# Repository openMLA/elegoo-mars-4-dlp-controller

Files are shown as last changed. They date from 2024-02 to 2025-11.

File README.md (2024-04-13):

# Raspberry Pi hat for Elegoo Mars 4 DLP board 

A hat for the raspberry pi that allows a resin 3D printer's **UV light** projector to be controlled. Note that this is (in direct form) only suitable for the projector in the Mars 4 DLP. If you have other boards check out the repository for the [Anycubic Photon Ultra](https://github.com/openMLA/photon-ultra-controller), or get in touch for modifications needed. 

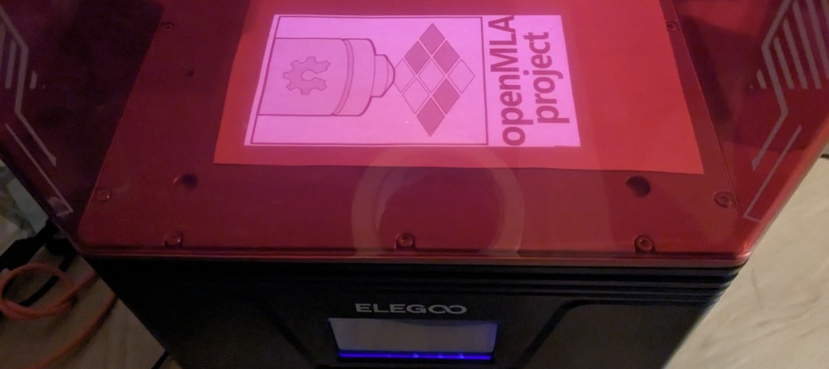
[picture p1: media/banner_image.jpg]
banner image showing custom image being displayed on the UV projector


The designs in this repository then allow you to project arbitrary **2560x1440** images with UV light on a surface. The native projected pixel size is **50μm**, making PCB fabrication an interesting application. All you would need is a bit of glue code to convert the Gerber files to a rasterised image and then you could easily use the existing 3D printer frame to expose PCB boards. Since you have all the files and access to the code, you can easily tune it to whatever production needs you have.

The UV projector of the Elegoo Mars 4 DLP is [developed and produced by Anhua (D63ZS50B)](https://www.anhuaoe.com/en/industriause/info.aspx?itemid=2694), and seems to be this variety. Under the hood it uses the Texas Instruments DLP300s or DLP301s digital micromirror array.

> [!NOTE]  
> While PCB fabrication is the most straightforward application for this board, this is actually developed as part of an effort towards an open hardware photolithography system. Check out the [openMLA organisation](https://github.com/openMLA/) for more info.

> If you have a projector using the DLPC1438 that uses the parallel video interface (rather than SPI) then you can check out the [PCB design and implementation for the Anycubic Photon Ultra](https://github.com/openMLA/photon-ultra-controller) projector.

### 🚀 At a glance

Running an SPI clock of ~125MHz it takes:

* ~0.75s to send a full 1440p image to the projector
* ~0.18s to send a 720p image to projector

Arbitrary sections of the display can be updated for even shorter transfer times. Note the maximum framerate (below) and that due to technical reasons the smallest image block that can be sent (in terms of transfer size) is 128x2 pixels. 

The image is stored in a buffer in the FPGA, so you can incrementally build or update an image, if that saves you time or makes your life easier.

The max achievable framerate seems to be about 10Hz (as there are some artefacts if you update faster). This is not a hard limit I suspect, and it may be possible to get closer to the display signal framerate of 60Hz.

### 💡 Sourcing the Projector

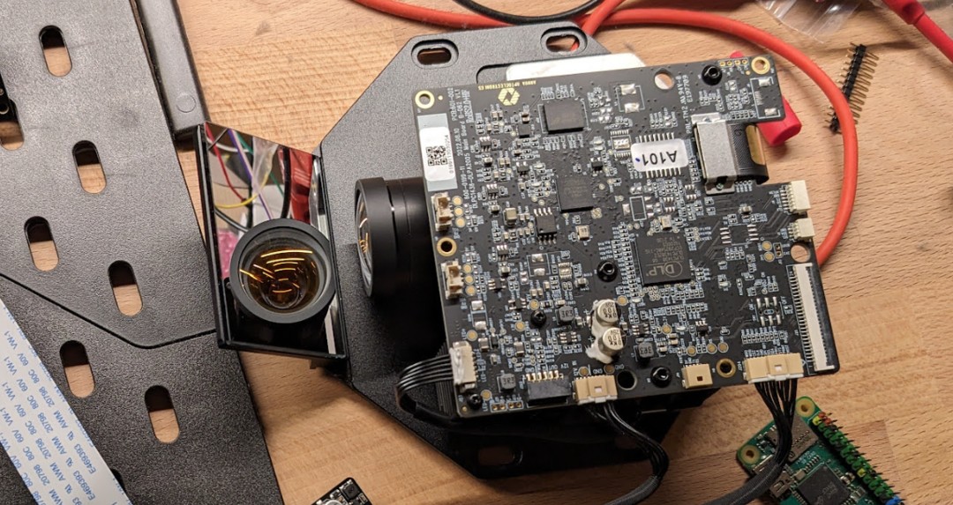
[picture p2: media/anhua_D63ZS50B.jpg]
the anhua projector taken from the Elegoo Mars 4 DLP


The easiest and cheapest way to source the projector is to buy a Elegoo Mars 4 DLP. At the time of writing (2024-02-02) the resin printer can be purchased in the EU for 275 euro (discounted).

Alternatively, the projector can be purchased directly from Anhua; but there may be small differences in the heatsink, LED source and other items. Also expect to pay a premium due to shipping, broker cost etc.

### 📃 Project BOM

The total costs for the project consists of 3 parts:

| Expense Description        | Cost  |
| -------------------------- | ----- |
| Elegoo Mars 4 DLP          | 274   |
| Electronics/PCB            | 52.38 |
| Enclosure/3D printed parts | -     |

_The PCB costs are further broken down [in the BOM in the PCB directory](./PCB/README.md)_

### 🎁 3D printable enclosure

A basic 3D printable enclosure is available in the enclosure directory. 

### 🛠 Disassembly 

Disassembly of the printer is not difficult, but I suggest you take a look at the points below before starting.

1. Make sure the projector is working properly by running the display test functions on the original elegoo board.
2. Raise the Z axis all the way to the top. It will only get in the way otherwise. You can also completely remove it later.
3. Remove the front panel. You will need allen keys and philips head screwdrivers. Carefully disconnect the display ribbon cable. Now you should be able to reach the connectors on the mainboard.
4. Disconnect all the connectors on the elegoo mainboard (the one not on top of the projector unit).
5. Undo the screws holding the bottom section of the printer enclosure in place. Now you carefully try to slide it forward and out of the way of the projector. This can be a bit tricky.
6. [optional] If don't want to use the projector in the original elegoo enclosure, you can remove it from the case with the 4 philips head screws holding it in place.

### 🛠 Assembly 

Assembly of the board is pretty straightforward. For completeness, here are the steps you will need to take.

1. Solder headers onto raspberry pi zero.
2. Assembly the custom PCB
3. Flash Raspberry Pi OS Lite onto an micro SD card. You can use [the raspberry pi imager](https://www.raspberrypi.com/software/) for this. Make sure to configure the wireless connection and ssh access in this step.
4. Attach the custom PCB to the raspberry pi zero header.
5. Plug in the 2 pico-claps connectors that were connected to the original elegoo mainboard
6. Plug in the original elegoo power supply to the barrel jack on the custom PCB.
7. Follow the more detailed [software setup](software-setup.md) to get the Pi up and running. 
8. [optional] if you want to use the projector inside the original enclosure, you can check out the instructions in [the enclosure directory](./enclosure/README.md)

### ✅ Future plans

2. Polish package with proper debug level logging and maybe proper formatted python documentation.
3. Add CRC16 checks. (low priority)

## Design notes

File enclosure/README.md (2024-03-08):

# Simple PCB Enclosure

To protect the raspberry pi zero and the PCB from damage and shorts you can 3D print the enclosure files in this directory.

Designed in FreeCAD. PCB was imported into FreeCAD with the [KiCAD StepUp plugin](https://www.kicad.org/external-tools/stepup/).

Step files can be sliced in e.g. PrusaSlicer.

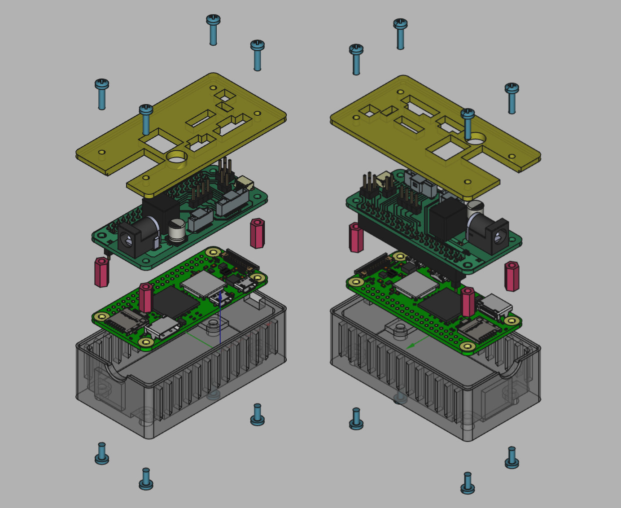
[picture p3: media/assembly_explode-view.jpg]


### Fasteners

In order to put this together you will also need:

* 4X M2.5 6mm screw
* 4X M2.5 10mm screw
* 4X DIN 6334 M2.5 10mm coupling nuts

### Using the enclosure inside the original Elegoo 3D printer

An alternative `.step` exists that has some extra mounting points that can mount onto the mounting points of the Projector.  That one is recommended if you want to keep using the 3D printer as a base for your project. You can of course also just print the normal case file and glue/tape it in place somewhere inside the case.

Some tips for assembling:

1. Tape the stepper, endswitch and USB power cables somewhere off to the side. Otherwise they may end up blocking the light from the projector.
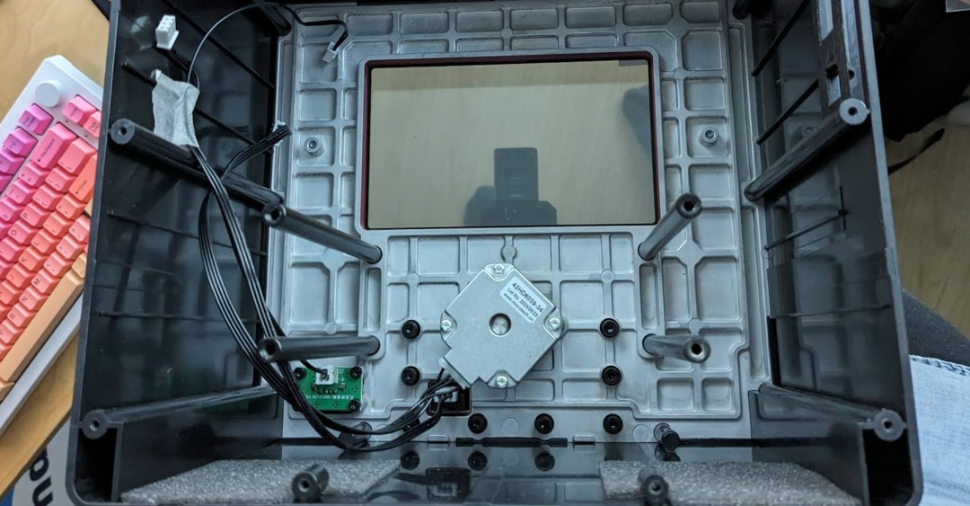
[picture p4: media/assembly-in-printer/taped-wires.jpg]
   
2. Avoid straining the pico-clasp cables
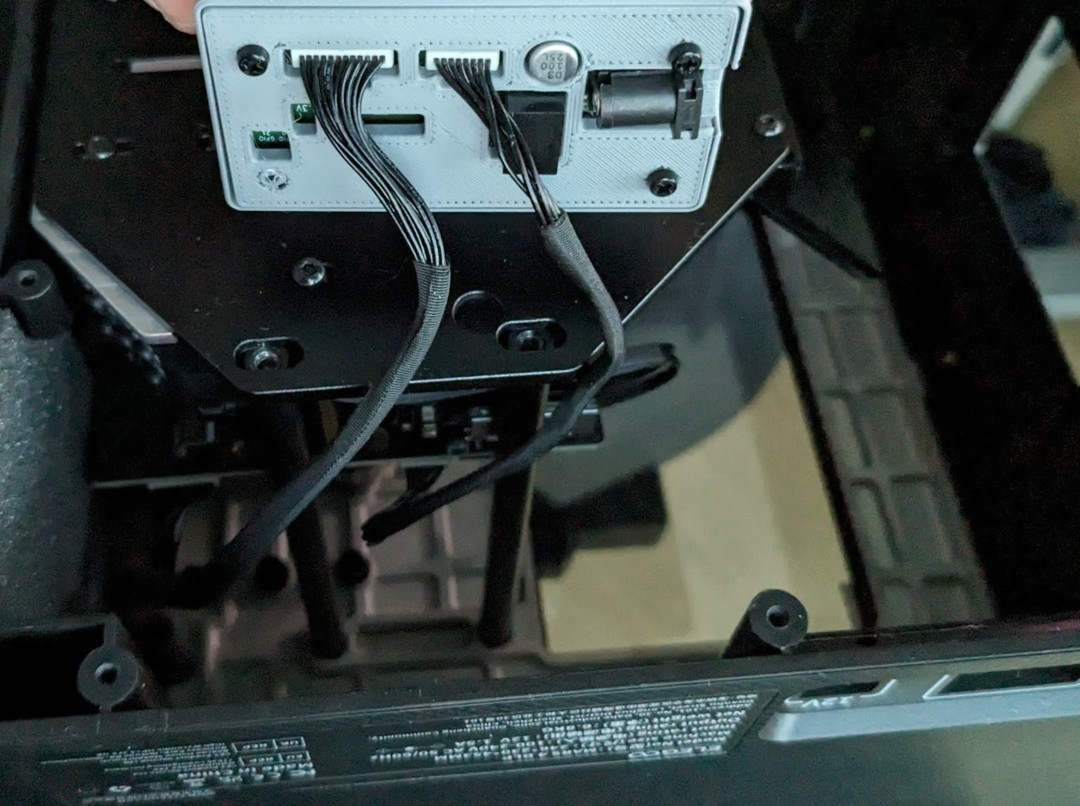
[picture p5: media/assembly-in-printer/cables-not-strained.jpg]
   
3. Route the original 12V power supply through one of the now open ports. It's not very elegant, so if you are interested you can modify the PCB or the case design to nicely route the power cable
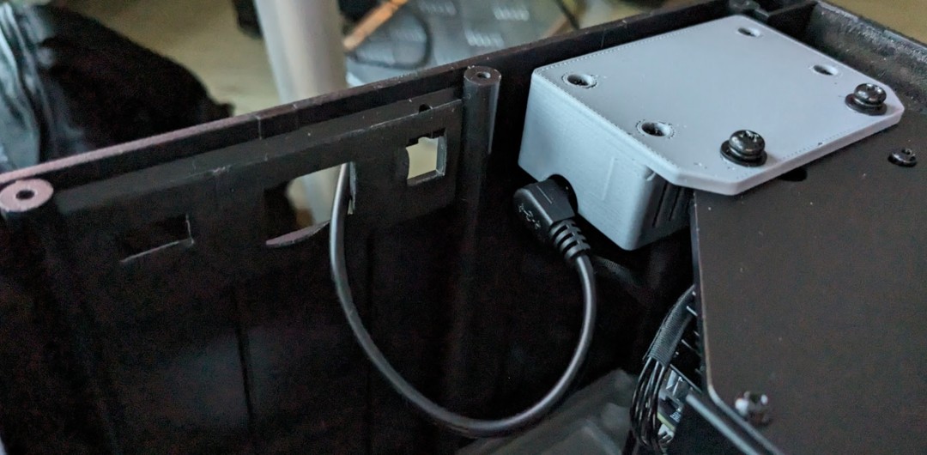
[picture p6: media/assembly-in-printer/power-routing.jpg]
   
4. Tape these open ports shut, to prevent leakage of UV light.
5. Keep the original touchscreen in place on the unit, as it will block the UV light. If you want to be extra secure, you can also apply some tape to the edges of the screen to really prevent UV leakage.

### External 3D models

The Model of the raspberry Pi zero 2 was downloaded from [the geekworm wiki](https://wiki.geekworm.com/Raspberry_Pi_Zero_2_W) on 28th of february 2023.

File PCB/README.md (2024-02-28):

# PCB design

To control the DMD with a raspberry pi, we need a very simple board that allows us to plug in the original Anhua board's connectors (Molex Pico-clasp). Check out [the schematic 🗺](elegoo-dlp-controller.pdf) for the quickest overview of all functionality.

To make our life a little easier, you can add an (optional) dc-dc converter that also converts the 12V to 5V and uses that to power the raspberry pi. This means you do not need to apply separate 5V power to the raspberry pi, and that the 12V needed for the Anhua board provided by the Elegoo Mars 4's power supply is enough to power everything.

Finally, the board breaks out some extra pins for adding your own extra custom bits. SPI and I2C connections, as well as some spare GPIO pins. This may be useful if you want to have exposure occur based on some sensor readout, or maybe tie UV exposure to a simple button for batch production where you don't want to send commands over SSH.

> [!IMPORTANT]  
> Not every connection has been verified to work. I suspect they are all fine since its not a very complex board or high frequency signals. At least the minimum set of pins required for data/exposure seem to work fine.

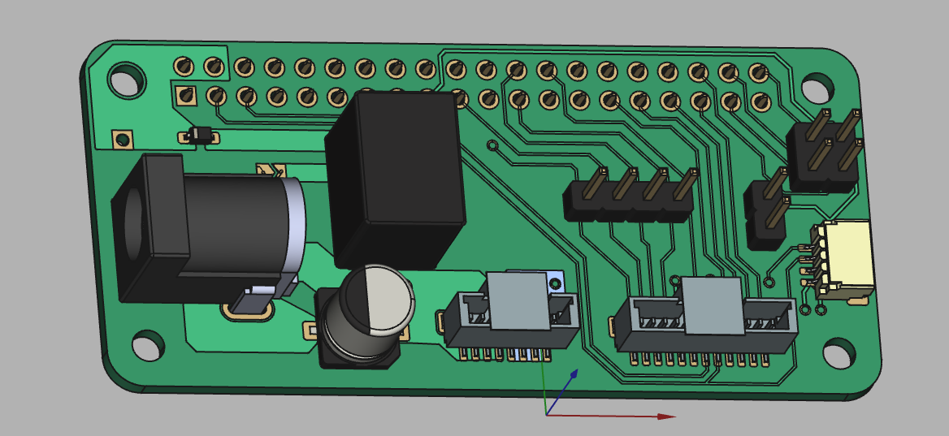
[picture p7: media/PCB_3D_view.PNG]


### Bill of materials

The costs below are indicative, as shipping cost and price changes may have occurred since writing this document. Check with KiCAD's schematic to see if it all up to date. All listed values are including taxes (21%).

| Description                | Supplier         | Supplier Part Number | Amount | Total Cost | Comment                                      |
| -------------------------- | ---------------- | -------------------- | ------ | ---------- | -------------------------------------------- |
| PCB manufacturing          | Aisler           |                      | 3      | 14         | MOC 3pcs                                     |
| Raspberry Pi Zero 2        | Mouser           | 358-SC0510           | 1      | 17         |                                              |
| Micro SD Card (32GB)       | Kiwi Electronics | TS32GUSDU1           | 1      | 10         | Whatever kind you want would work            |
| Raspberry pi header        | Kiwi Electronics | KW-2639              | 1      | 2          | or any basic, cheaper header                 |
| Raspberry pi header female | Kiwi Electronics | KW-1650              | 1      | 1.5        |                                              |
| JST SH 4-pin               | Mouser           | 474-PRT-14417        | 1      | 0.67       | Optional, allows i2c through  stemmaQT/QWIIC |
| Molex PicoClasp 12 pin     | Mouser           | 538-501331-1207      | 1      | 1.19       |                                              |
| Molex PicoClasp 8 pin      | Mouser           | 538-501331-0807      | 1      | 0.92       |                                              |
| Cui DC-DC converter        | Mouser           | 490-P78E05-1000      | 1      | 3.45       |                                              |
| Barreljack                 | Mouser           | 490-PJ-002B          | 1      | 0.79       |                                              |
| Schottky Diode             | Mouser           | 771-PMEG1020EJ-T/R   | 1      | 0.29       |                                              |
| 100uF capacitor            | Mouser           | 667-EEE-FN1E101UP    | 1      | 0.57       |                                              |
|                            |                  |                      |        |            |                                              |
| Total                      |                  |                      |        | 52.38      |                                              |

### Miscellaneous

* Board was designed in KiCAD 7.0
* I had the board fabricated at Aisler (Germany), at 14 euros (total) for 3 boards.

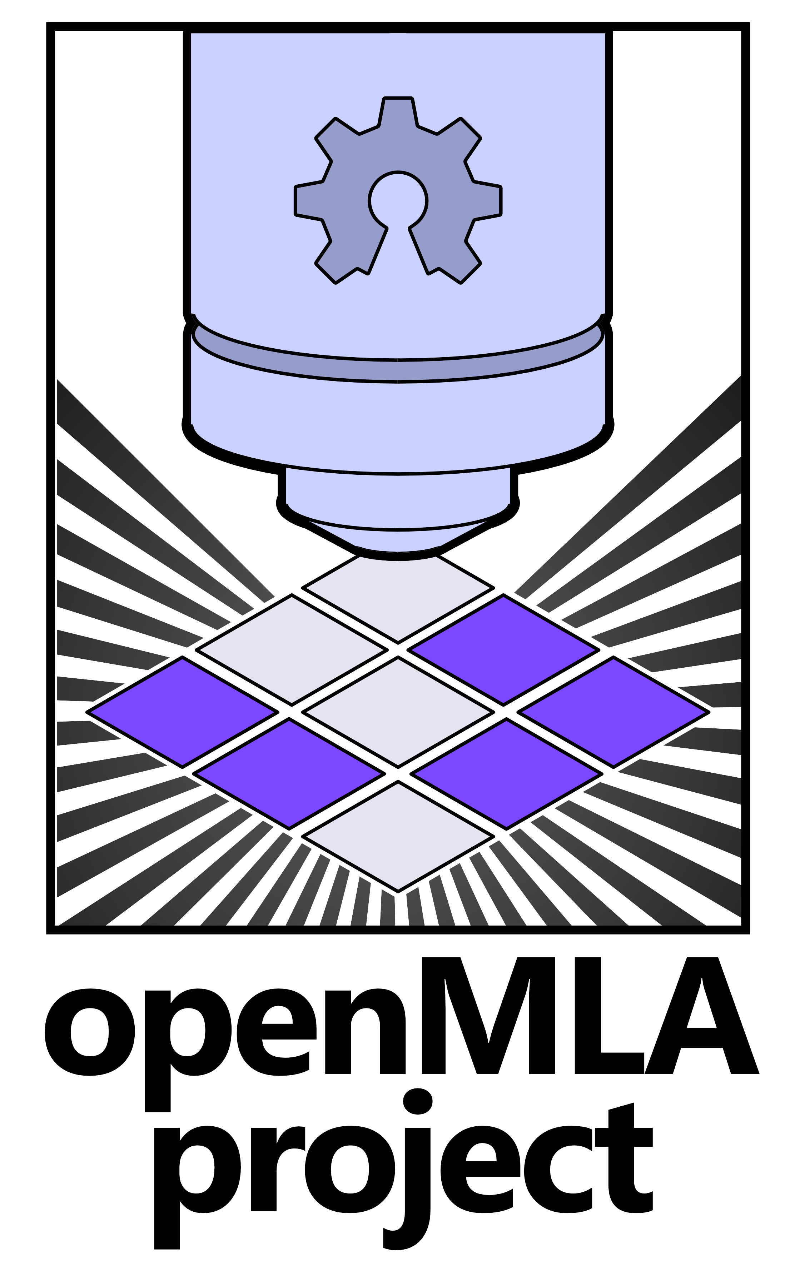
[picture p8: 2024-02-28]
PCB/board-assets/open-mla-tall - Copy.png

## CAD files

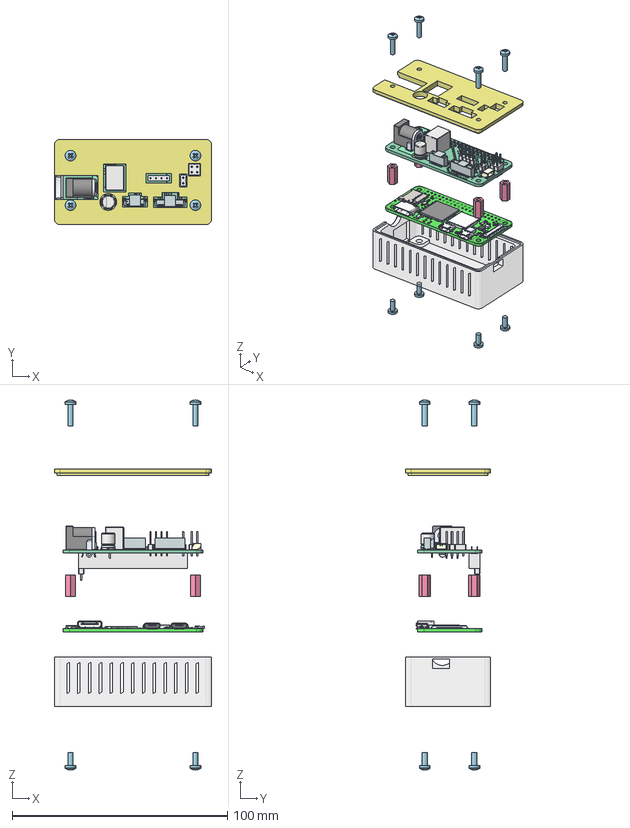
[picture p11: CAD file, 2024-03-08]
enclosure/dlp-controller-enclosure.FCStd
73.0 x 39.5 x 171.8 mm
enclosure-base
PCB, Raspberry Pi Zero 2 W
RP3A0-AU 2105 201221C, Raspberry Pi Zero 2 W
MicroUSB Port, Raspberry Pi Zero 2 W
MicroUSB Port, Raspberry Pi Zero 2 W001
MicroUSB Port, Raspberry Pi Zero 2 W002
MicroUSB Port, Raspberry Pi Zero 2 W003
MicroUSB Port, Raspberry Pi Zero 2 W004
MicroUSB Port, Raspberry Pi Zero 2 W005
MicroUSB Port, Raspberry Pi Zero 2 W006
SD Card Slot, Raspberry Pi Zero 2 W
SD Card Slot, Raspberry Pi Zero 2 W001
SD Card Slot, Raspberry Pi Zero 2 W002
SD Card Slot, Raspberry Pi Zero 2 W003
SD Card Slot, Raspberry Pi Zero 2 W004
SD Card Slot, Raspberry Pi Zero 2 W005
SD Card Slot, Raspberry Pi Zero 2 W006
SD Card Slot, Raspberry Pi Zero 2 W007
SD Card Slot, Raspberry Pi Zero 2 W008
SD Card Slot, Raspberry Pi Zero 2 W009
Wireless Module Cover, Raspberry Pi Zero 2 W
Crystal Resonator, Raspberry Pi Zero 2 W
LED, Raspberry Pi Zero 2 W
Diode, Schottky, Raspberry Pi Zero 2 W
54548-2271, 22 Pin FPC Connector, Raspberry Pi Zero 2 W
Mini HDMI Receptacle Port, Raspberry Pi Zero 2 W
PAM2306AYPKE, Switching Voltage Regulators Dual PWM Step-Down 40uA 1A 1.5MHz, Raspberry Pi Zero 2 W
RT9081A-1BGQZA, Fixed LDO Voltage Regulator, 0.8V-5.5Vin, 140mV drop, 1.25Vout, 0.5Aout, Raspberry Pi Zero 2 W_default
RT8088AWSC, IC Reg Buck Prog 3A Sync 15WLCSP, Raspberry Pi Zero 2 W_default
SMD Inductor, Configurable, Raspberry Pi Zero 2 W_L1
SMD Inductor, Configurable, Raspberry Pi Zero 2 W_L2
SMD Capacitor, Configurable, Raspberry Pi Zero 2 W_C1
SMD Capacitor, Configurable, Raspberry Pi Zero 2 W_C002
SMD Capacitor, Configurable, Raspberry Pi Zero 2 W_C003
MicroUSB Port, Raspberry Pi Zero 2 W008
MicroUSB Port, Raspberry Pi Zero 2 W009
MicroUSB Port, Raspberry Pi Zero 2 W010
MicroUSB Port, Raspberry Pi Zero 2 W011
MicroUSB Port, Raspberry Pi Zero 2 W012
MicroUSB Port, Raspberry Pi Zero 2 W013
MicroUSB Port, Raspberry Pi Zero 2 W014
SMD Capacitor, Configurable, Raspberry Pi Zero 2 W_C3
SMD Capacitor, Configurable, Raspberry Pi Zero 2 W_C005
SMD Capacitor, Configurable, Raspberry Pi Zero 2 W_C006
SMD Capacitor, Configurable, Raspberry Pi Zero 2 W_C008
SMD Capacitor, Configurable, Raspberry Pi Zero 2 W_C009
SMD Capacitor, Configurable, Raspberry Pi Zero 2 W_C010
SMD Capacitor, Configurable, Raspberry Pi Zero 2 W_C012
SMD Capacitor, Configurable, Raspberry Pi Zero 2 W_C013
SMD Capacitor, Configurable, Raspberry Pi Zero 2 W_C014
SMD Capacitor, Configurable, Raspberry Pi Zero 2 W_C016
SMD Capacitor, Configurable, Raspberry Pi Zero 2 W_C017
SMD Capacitor, Configurable, Raspberry Pi Zero 2 W_C018
SMD Capacitor, Configurable, Raspberry Pi Zero 2 W_C020
SMD Capacitor, Configurable, Raspberry Pi Zero 2 W_C021
SMD Capacitor, Configurable, Raspberry Pi Zero 2 W_C022
SMD Capacitor, Configurable, Raspberry Pi Zero 2 W_C024
SMD Capacitor, Configurable, Raspberry Pi Zero 2 W_C025
SMD Capacitor, Configurable, Raspberry Pi Zero 2 W_C026
SMD Capacitor, Configurable, Raspberry Pi Zero 2 W_C028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

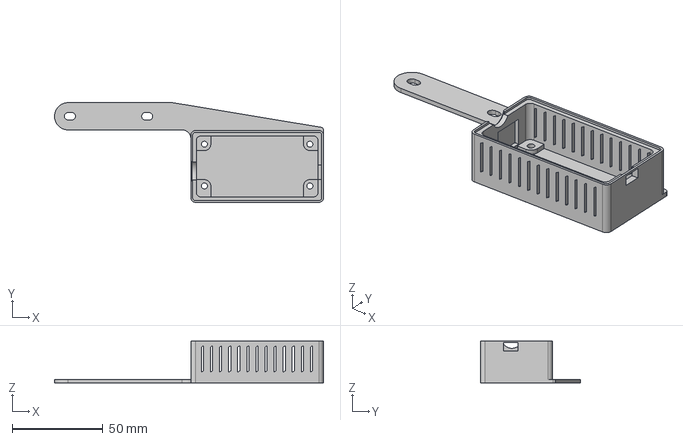
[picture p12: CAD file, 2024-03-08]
enclosure/step/enclosure-base-elegoo.step
148.0 x 54.9 x 23.0 mm

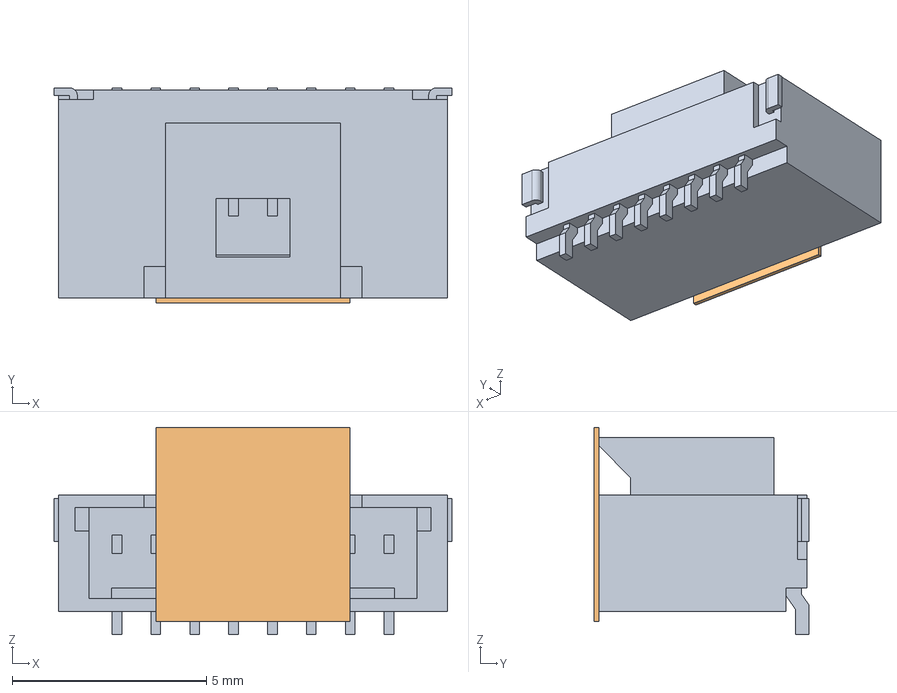
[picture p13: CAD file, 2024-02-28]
PCB/board-assets/molex_5013310807.stp
10.2 x 5.54 x 5.34 mm

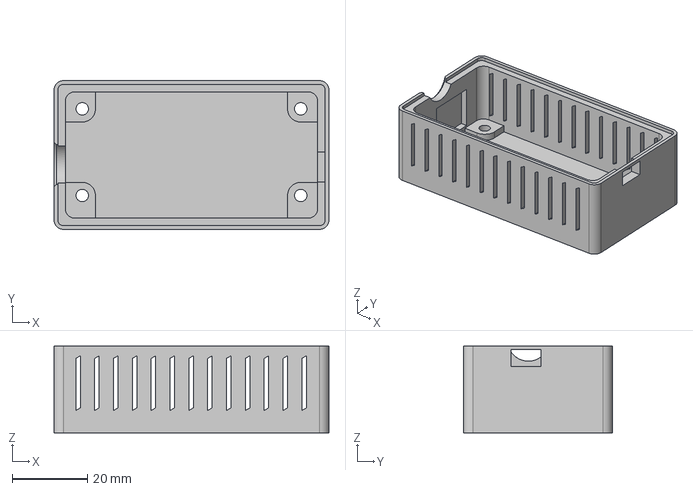
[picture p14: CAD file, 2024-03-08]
enclosure/step/enclosure-base.step
73.0 x 39.5 x 23.0 mm

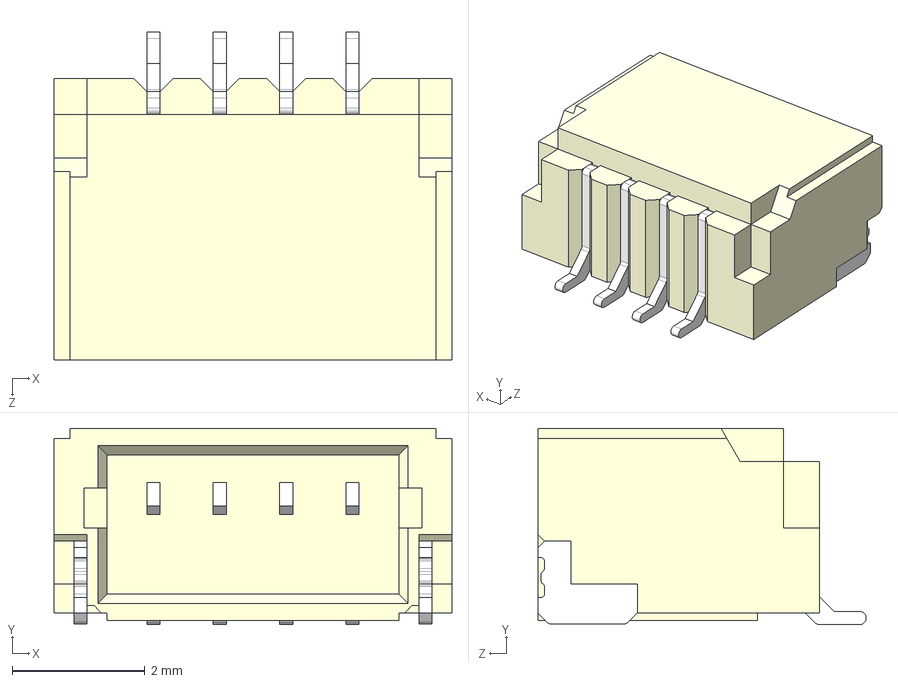
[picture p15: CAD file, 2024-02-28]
PCB/board-assets/PRT-14417--3DModel-STEP-SnapEDA.STEP
6.00 x 2.96 x 4.95 mm

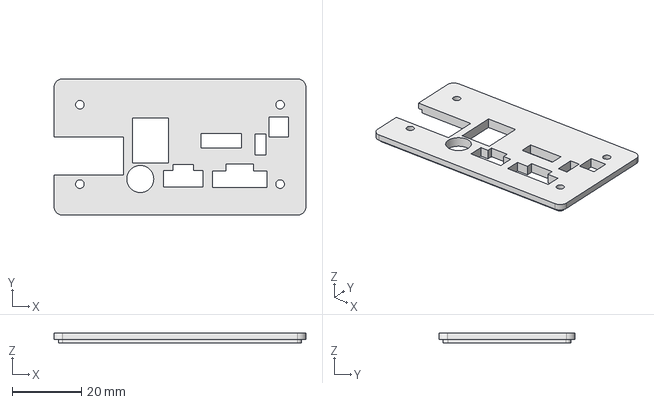
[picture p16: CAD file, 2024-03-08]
enclosure/step/enclosure-lid.step
73.0 x 39.5 x 3.00 mm

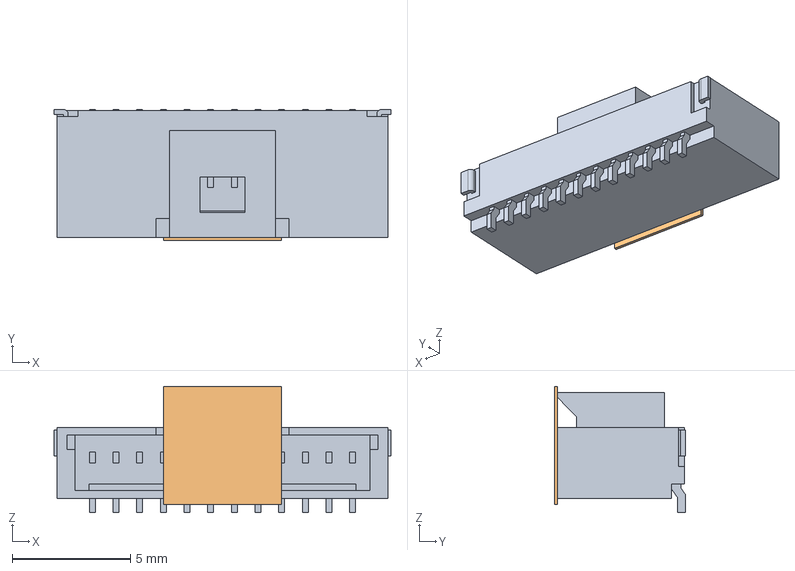
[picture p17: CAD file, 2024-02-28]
PCB/board-assets/molex_5013311207.stp
14.2 x 5.54 x 5.34 mm

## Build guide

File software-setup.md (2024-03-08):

## ⚙ configuring the Raspberry Pi for project

> [!NOTE]
>
> The following set of instructions assumes you are running Raspberry Pi OS Lite. 

We will need to get pip. Doesn't seem to get packaged by default.

```shell
sudo apt install python3-pip
```

and we need to enable I2C and SPI with the following commands

```shell
sudo raspi-config nonint do_i2c 0
```

```shell
sudo raspi-config nonint do_spi 0
```

We also need to increase the SPI buffer size, as the default is only 4096 bytes. To do so, we edit `cmdline.txt` by running

```shell
sudo nano /boot/cmdline.txt
```

and we add the following entry to increase the buffer size to 65536  bytes:

```
spidev.bufsiz=65536  
```

> [!IMPORTANT]
>
> Note that after setting these new values you will need to restart the raspberry pi for the changes to go into effect.

#### 🐍 Python packages

Finally, we will need to install some python packages:

```shell
sudo apt install python3-smbus
```

```shell
sudo apt install python3-spidev
```

```shell
sudo apt install python3-numpy
```

```shell
sudo apt install python3-pillow
```

> [!NOTE]
>
> For some reason Pi OS Lite doesn't love installing via pip, so the commands above are used. I am sure you could install it via pip with minimal effort.

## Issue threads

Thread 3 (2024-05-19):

### ISSUE TITLE
Using Rasbian Pi OS (64bit)

### ISSUE THREAD

**Issue by Hackerman2016** [openMLA/elegoo-mars-4-dlp-controller#3]
In the project, you have used the Rasbian Pi OS Lite. I was wondering if there is any specific reason for that. can I use the Rasbian Pi OS (64bit) instead, and would the same Python script work for that? Also, will the commands for installing Python libraries remain the same? Any help with this would be great. Thanks!

**Comment by NemoAndrea** [comment]
The normal raspberry Pi OS should work fine. It may be that the normal OS already has some of the dependencies installed (which isn't bad). I use the Lite version because I don't need a desktop environment anyway (just accessing the Pi over SSH), so then the Lite version will give better boot times and performance.

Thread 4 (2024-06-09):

openMLA/elegoo-mars-4-dlp-controller #4: Soldering 5V port on PCB

Hackerman2016, 2024-06-09:
So I have built the PCB according to the instructions, and I was wondering whether or not to solder the 5V port on the PCB, and after the PCB is complete, what is ideally the next step? I have to install the packages as specified on the pi and run the main.py, and it should work?

NemoAndrea, 2024-06-09:
The 5V pin on the PCB (assuming we are talking about the same pin), can be left out; it is just there in case you want to power something with the 5V from the pi/dcdc converter. 

If you are taking about the solder bridge: it should be soldered if you have a the  dc-dc converter (CUI P78E)  soldered in place; if you don't have the CUI, then it doesn't really matter if you close the solder bridge. 

> [!WARNING]
> Whatever you do, do not power the raspberry pi through USB and the CUI converter at the same time. It is **either** power through the USB connector of the pi (leave the 5V solder bridge empty, and leave out the CUI) **or** power through the 12V barrel jack with the CUI to provide the 5V power for the Pi.

If you have assembled the board and checked that the pi still works (I suggest you do this before connecting the projector). then you hook up the projector, follow the software packages instructions and then indeed try main.py.

If that all works you can start writing your own python code for your project  using the included code :)

Hackerman2016, 2024-06-10:
I have the dc-dc converter in place.
[image]
This is the 5V port I am talking about.

NemoAndrea, 2024-06-10:
Ah yes, that one you should bridge if you have the dc-dc converter installed. This connects the 12V to the input of the converter. 

To reiterate (to prevent damage), do not connect USB power to the pi if you also connect the 12V at the same time.

Hackerman2016, 2024-06-11:
Ah, okay. Great. Thanks a lot.

closed 2024-06-11 by Hackerman2016

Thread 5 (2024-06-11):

openMLA/elegoo-mars-4-dlp-controller #5: Regarding running the python code

Hackerman2016, 2024-06-11:
[image]

I have connected all the components and have managed to power on the printer after connecting the pcb and pi but as soon as I run the code I get this error. Any help with this will be appreciated. Also I have trouble in connecting the pi to the internet. Doing configuring the rasbian os 64 bit on the pi zero 2W I did the ssh settings but still somehow when I login on putty with the hostname I get an error saying hostname doesn't exist.

Hackerman2016, 2024-06-11:
Also when I am trying to increase the SPI buffer size I followed the steps mentioned in the document but I am unable to do it. I am getting this error.
[image]

NemoAndrea, 2024-06-25:
Hmm for the first point, could it be that you are running the python code on your local machine and not on the raspberry pi? If not then you need to install RPi.GPIO but I think that should definitely come with the default OS.

For the 2nd image, why is there `firmware` in the path?  It should just be `/boot/cmdline.txt`; that might fix it

Hackerman2016, 2024-06-26:
For the first point you were right I was trying to run it on local machine. Running it on Pi solved the issue and yeah about making changes in the /boot/cmdline.txt file, for me after running that command I get an error saying that the file has been shifted to /boot/firmware/cmdline.txt. That's why increasing the buffer size and stuff I have all done it in that file.

NemoAndrea, 2024-06-26:
Hmm, strange, I am not aware of this change. I guess there must be a file `cmdline.txt` somewhere on the system. Maybe you can post raspberry pi os version here, so that other people can figure out if they may be running a version with issues too.

Hackerman2016, 2024-06-27:
That is a difference I am not working with the OS lite and Pi Zero. I am working with the Raspberry Pi 3b+ and the standard Raspberry OS 64-bit.

NemoAndrea, 2024-08-06:
Okay, I will close this issue, as I think it would be better to make a more focussed new issue if you cannot figure it out. Nice to see you being able to get the project working (at least in parts!). 

If you run into issues where the documentation is wrong or even just unclear, let me know because that is super valuable for the project :)

closed 2024-08-06 by NemoAndrea

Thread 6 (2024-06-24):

openMLA/elegoo-mars-4-dlp-controller #6: Error while reading i2c port 1

Hackerman2016, 2024-06-24:
Hello,

I am trying to run the python script and I am getting an error where the i2c 1 port is undetectable.  I have tried adding these lines in the boot file 'dtparam=i2c_arm=on
dtparam=i2c1=on'   

Still I get the same error. Here is the error that I get:

  File "/home/pi/Desktop/UV_projector/controller.py", line 61, in __init__
    i2c_bus.read_byte(self.addr)  # check if i2c is already active. Then we are in [2]
    ^^^^^^^^^^^^^^^^^^^^^^^^^^^^
OSError: [Errno 5] Input/output error

During handling of the above exception, another exception occurred:

Traceback (most recent call last):
  File "/home/pi/Desktop/main.py", line 24, in <module>
    DMD = DLPC1438(i2c, spi)
          ^^^^^^^^^^^^^^^^^^
  File "/home/pi/Desktop/UV_projector/controller.py", line 85, in __init__
    while i2c_bus.read_byte(self.addr) == 0:  
          ^^^^^^^^^^^^^^^^^^^^^^^^^^^^
OSError: [Errno 5] Input/output error

NemoAndrea, 2024-06-25:
hmm, what does `i2cdetect -y 1` give?

Hackerman2016, 2024-06-26:
It gives a table where there are no addresses assigned. So it is just a table with dashes.

NemoAndrea, 2024-06-26:
Okay, so that means that the I2C hardware on the Pi is working.  I don't really know what is causing the issue; it certainly seems like the DLPC1438 is not starting properly. Do you see some LEDs lit up on the mainboard? Does it work if you run the code a few times (Sometimes it needs one run to get going; something not quite right about the power up cycle in the code)

Hackerman2016, 2024-06-28:
[image]

Do i need to solder these adapters too on the pcb or are they optional? What are their functions?

NemoAndrea, 2024-07-17:
> ![image0 (2)](https://private-user-images.githubusercontent.com/170014411/344107721-8f8bc00e-e9fa-4d8c-bf7a-1d914d15774f.jpeg?jwt=eyJhbGciOiJIUzI1NiIsInR5cCI6IkpXVCJ9.eyJpc3MiOiJnaXRodWIuY29tIiwiYXVkIjoicmF3LmdpdGh1YnVzZXJjb250ZW50LmNvbSIsImtleSI6ImtleTUiLCJleHAiOjE3MjEyMTc4NjcsIm5iZiI6MTcyMTIxNzU2NywicGF0aCI6Ii8xNzAwMTQ0MTEvMzQ0MTA3NzIxLThmOGJjMDBlLWU5ZmEtNGQ4Yy1iZjdhLTFkOTE0ZDE1Nzc0Zi5qcGVnP1gtQW16LUFsZ29yaXRobT1BV1M0LUhNQUMtU0hBMjU2JlgtQW16LUNyZWRlbnRpYWw9QUtJQVZDT0RZTFNBNTNQUUs0WkElMkYyMDI0MDcxNyUyRnVzLWVhc3QtMSUyRnMzJTJGYXdzNF9yZXF1ZXN0JlgtQW16LURhdGU9MjAyNDA3MTdUMTE1OTI3WiZYLUFtei1FeHBpcmVzPTMwMCZYLUFtei1TaWduYXR1cmU9ZDZkYTRiOWJhNDcyMjA0ODJmY2NmNzczMTM1OTYzNWYwOWJjNTlkZTQ0OTRiMTg1NDRlOGFiZGY4ZGU2NDRmOCZYLUFtei1TaWduZWRIZWFkZXJzPWhvc3QmYWN0b3JfaWQ9MCZrZXlfaWQ9MCZyZXBvX2lkPTAifQ.KolqDCWs3LSlLgdFGFEeP9A25HvDo95ajfdwG2wfoAs)
> 
> Do i need to solder these adapters too on the pcb or are they optional? What are their functions?
> 
> Also does any pin or cable go into the adapter labelled i2c, cause I can't seem to find any that go in that.

Those circled solder points are indeed optional :). They can be used if you find you need those pins for something else (e.g. you want to connect to another SPI peripheral or need some 3.3V power for something).

The I2C connector on the right side in your image is also there just as an optional extra; if you want to connect one of the many i2c breakout boards that use a StemmaQT/QWIIC connector. But it is not needed for operation of the DMD unit.

NemoAndrea, 2024-07-17:
> I did running the code 3-4 times, still same error. That is what I am wondering, that i2cdetect -y 2 shows address and -y 1 doesn't. Does that mean one of the ports is working and one isn't? (1 of the 2 picoclasps that we connect on the pcb). I have tried running test scripts for the 2nd port and they work correctly so I think there has to be maybe an issue on the hardware soldering side or in the connections on the pcb.
> 
> Also yeah LEDs on the DLPC1438 do light up for a while and then after I get the error they turn off.

Hmm this is interesting, I will check if maybe I use i2c bus 2 and forgot to add that to documentation.

Okay, the LED on the DLPC1438 board turning off means that at least one of the hardware connections from the picoclasp is working OK).

NemoAndrea, 2024-07-18:
> I did running the code 3-4 times, still same error. That is what I am wondering, that i2cdetect -y 2 shows address and -y 1 doesn't. Does that mean one of the ports is working and one isn't? (1 of [...]

From what I gather, /dev/i2c/2 is the i2c data for the HDMI connector, and is therefore not showing the board data. /dev/i2c/1 (what you see by `i2cdetect -y 1`) should be i2c bus that you need. That one is also the one the code uses.

So it seems that for whatever reason the elegoo board is not showing up on the i2c bus. That could be for various reasons: the i2c connection having issues, the elegoo board not starting due to faulty connections, the elegoo board not starting because it is damaged etc.  It is a bit surprising since the board is responding to the code - so maybe that points to the i2c connection soldering being off?

Hard to say without really probing the board itself I think. You could doublecheck the solder connections and see if there is anything wrong.

Hackerman2016, 2024-07-31:
Yes indeed, there was a problem with one of pins when I soldered them, fixing that resolved the issue, thanks.

closed 2024-07-31 by NemoAndrea

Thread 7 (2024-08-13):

openMLA/elegoo-mars-4-dlp-controller #7: Programming the Stepper Motor for the Printer

Hackerman2016, 2024-08-13:
I am thinking of also controlling the stepper motor to control the Z stage of the printer but I don't think I can just connect the pins to the custom pcb and modify the python script to run it. Would connecting the stepper motor pins to an Arduino and then somehow configuring that arduino also with the same Raspberry Pi be a solution?

NemoAndrea, 2024-08-14:
The board should have a few spare GPIOs that you can solder headers to. Those you can then use to output step/dir signals over. You would need a simple stepper driver board that takes that output and manages the power delivery and phases for the stepper; but these kinds of boards are very cheap and common. I guess you would need to check a bit that the driver can manage the particular motor used in the elegoo unit.

Hackerman2016, 2024-08-15:
[image]

Do you mean connecting the cables here on this header? I tried directly connecting it on the pcb but I think I will have to find a driver board.

NemoAndrea, 2024-08-15:
Yes, those pins are connected to some GPIO pins (check the PCB schematic to find out which ones). These can provide the directional signal for the stepper, but definitely not the power required to actually actuate the stepper motor. For that indeed you need a little driver board.  You may need to get a bit creative with soldering if the stepper needs 12V (as I didn't put a nice header for the 12V output I think...

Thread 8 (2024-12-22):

### ISSUE TITLE
Projector not quite working

### ISSUE THREAD

**Issue by davidsachs** [openMLA/elegoo-mars-4-dlp-controller#8]
I hooked everything up and followed the software setup instruction, the projector is projecting, but not projecting the patterns I expect, and a few things are not working. For example, if I run:

DMD.set_background(intensity=15, both_buffers = False)

I would expect the entire image to be darker, but it isn't. However, if I run the above line multiple times, then part of the image is darker, depending on how many times I run it. So this suggests to me that something is weird with the SPI protocol and the splitting up of the data, or maybe of the end of the SPI command for each chunk. 

The image is also flickering, so it's possible there's a solder issue somewhere. But oddly if I run main.py, it projects a bunch of times (but just sort of turning on and off, not projecting images), and reliably flickers at the beginning of the program but not at the end. So could the flickering somehow be due to the software?

I'm also getting the "PRINT ACTIVE did not go high after starting exposure" error message.

Raspberry pi is 358-SC1146 from Mouser, running 32 bit Bullseye

**Comment by NemoAndrea** [comment]
Not that I think it would matter much, but are your running Raspberry OS lite, or with desktop?

I think the `PRINT ACTIVE` message can be ignored.

Some images may be useful for debugging. Here is a video of it working on my zero

Some flickering is expected i.i.r.c. as the unit targets a 30Hz or so refresh rate. I think there should be ways to avoid that, but for now that hasn't been something I have worked on.

https://github.com/user-attachments/assets/020fbf53-90c2-4a46-b2de-2d167c933b9b

**Comment by davidsachs** [comment]
It's the lite OS, not desktop.

I checked the connections with a multimeter and touched up the soldering, the behavior is the same. Maybe it's an SPI protocol issue?
Here's a video of main.py (the light is saturating my cell phone camera, so it looks a little weird)

https://github.com/user-attachments/assets/2da4987a-22ab-4abb-8392-633d9e833592

I also tried this code:
wtf = 15
for i in range(10):
    DMD.set_background(intensity = wtf, both_buffers = False)
    DMD.swap_buffer()
    DMD.expose_pattern(exposed_frames = -1)
    time.sleep(1)
    DMD.stop_exposure()
    time.sleep(1)
    DMD.swap_buffer()

It should do the same thing each time, but instead each iteration seems to set a slice of the background to 15:

https://github.com/user-attachments/assets/bbd94e8a-0b0c-454a-8bb9-6a63e59a6d17

**Comment by davidsachs** [comment]
All fixed now. I had set spidev.bufsize instead of spidev.bufsiz.

Thanks for building all of this!

**Comment by NemoAndrea** [comment]
Alright, nice that you found the source of the problem, and always good to hear that someone is able to replicate everything with the instructions! If you found anything unclear, or you had to do something that was not described in the docs, I would love to hear about it!

If you end up getting your project working, I'd also love to get a link or email to it!

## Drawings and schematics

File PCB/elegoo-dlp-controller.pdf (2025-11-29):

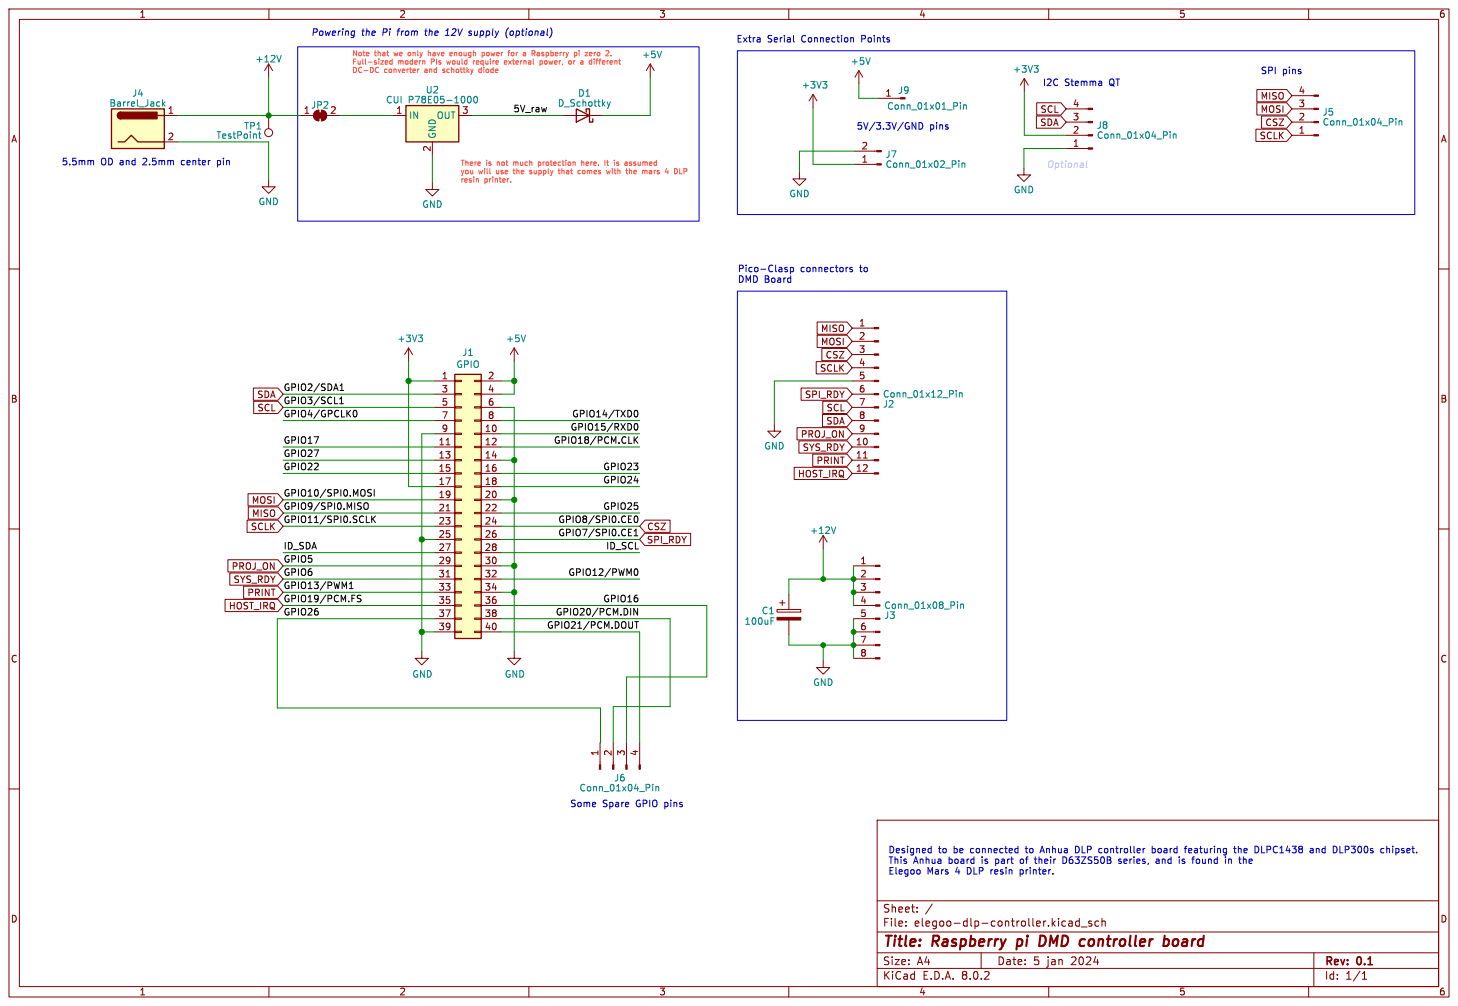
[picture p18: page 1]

you will use the supply that comes with the mars 4 DLP
resin printer.

Some Spare GPIO pins

File: elegoo-dlp-controller.kicad_sch Sheet: /
Id: 1/1 Title: Raspberry pi DMD controller board

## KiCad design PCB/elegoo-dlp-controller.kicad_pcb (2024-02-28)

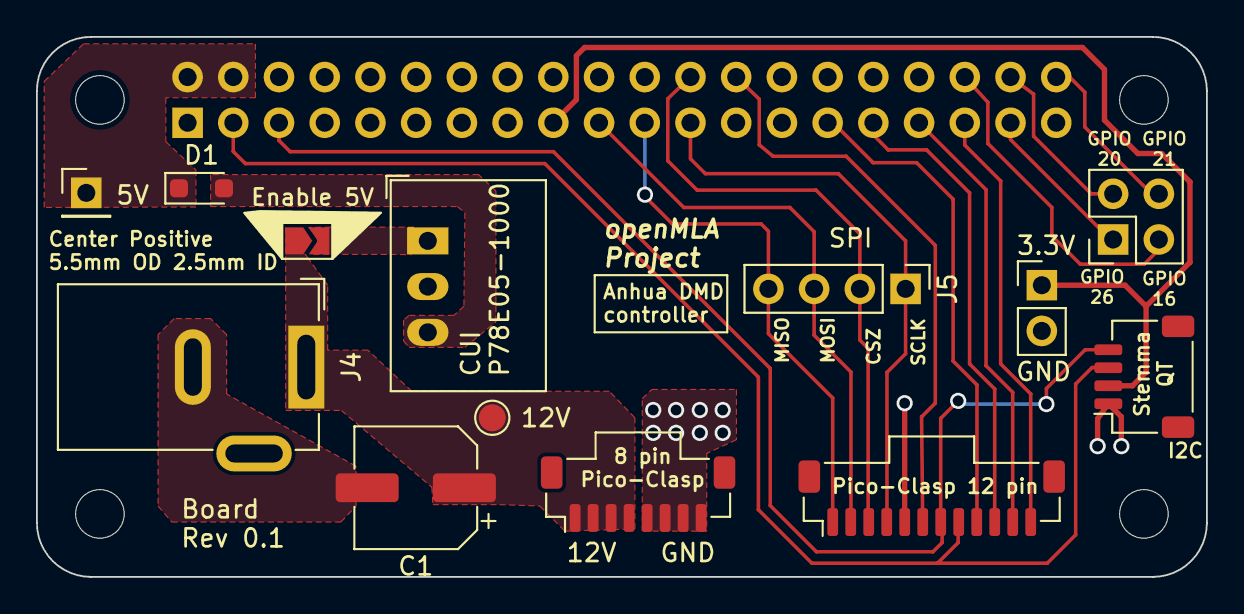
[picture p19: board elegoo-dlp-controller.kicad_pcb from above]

Board: 2 copper layers, 65.0 x 30.0 mm, 18 parts (1 on the bottom side), 21 nets.

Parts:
C1: 100uF; CP_Elec_6.3x7.7
D1: D_Schottky; D_SOD-323_HandSoldering
J1: GPIO; PinSocket_2x20_P2.54mm_Vertical
J2: Conn_01x12_Pin; Molex_Pico-Clasp_501331-1207_1x12-1MP_P1.00mm_Vertical
J3: Conn_01x08_Pin; Molex_Pico-Clasp_501331-0807_1x08-1MP_P1.00mm_Vertical
J4: Barrel_Jack; BarrelJack_GCT_DCJ200-10-A_Horizontal
J5: Conn_01x04_Pin; PinHeader_1x04_P2.54mm_Vertical
J6: Conn_01x04_Pin; PinHeader_2x02_P2.54mm_Vertical
J7: Conn_01x02_Pin; PinHeader_1x02_P2.54mm_Vertical
J8: Conn_01x04_Pin; JST_SH_SM04B-SRSS-TB_1x04-1MP_P1.00mm_Horizontal
J9: Conn_01x01_Pin; PinHeader_1x01_P2.54mm_Vertical
JP2: SolderJumper_2_Bridged; SolderJumper-2_P1.3mm_Open_TrianglePad1.0x1.5mm
MH1, MH2, MH3, MH4: MountingHole_2.7mm_M2.5
TP1: TestPoint; TestPoint_Pad_D1.5mm
U2: CUI P78E05-1000; Converter_DCDC_RECOM_R-78E-0.5_THT

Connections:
+3V3: J1.1, J1.17, J7.1, J8.2
+5V: D1.1 (K), J1.2, J1.4, J9.1
+12V: C1.1, J3.1, J3.2, J3.3, J3.4, J4.1, JP2.1 (A), TP1.1
/5V_raw: D1.2 (A), U2.3 (OUT)
/GPIO16: J1.36, J6.3
/GPIO20/PCM.DIN: J1.38, J6.2
/GPIO21/PCM.DOUT: J1.40, J6.4
/GPIO26: J1.37, J6.1
CSZ: J1.24, J2.3, J5.2
GND: C1.2, J1.6, J1.9, J1.14, J1.20, J1.25, J1.30, J1.34, J1.39, J2.5, J3.5, J3.6, J3.7, J3.8, J4.2, J7.2, J8.1, U2.2 (GND)
HOST_IRQ: J1.35, J2.12
MISO: J1.21, J2.1, J5.4
MOSI: J1.19, J2.2, J5.3
unnamed: JP2.2 (B), U2.1 (IN)
PRINT: J1.33, J2.11
PROJ_ON: J1.29, J2.9
SCL: J1.5, J2.7, J8.4
SCLK: J1.23, J2.4, J5.1
SDA: J1.3, J2.8, J8.3
SPI_RDY: J1.26, J2.6
SYS_RDY: J1.31, J2.10

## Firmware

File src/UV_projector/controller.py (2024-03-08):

import warnings
import RPi.GPIO as GPIO
import time
import enum
import math
import numpy as np

from UV_projector.img_convert import image_to_arr

class Mode(enum.IntEnum):
    STANDBY = 0xFF,
    EXTERNALPRINT = 0x06,
    TESTPATTERN = 0x01
    
class DLPC1438:
    """
    Representation of the DLPC1438 DMD controller. Communication between the user board (raspberry
    pi) and the DLPC1438+FPGA are handled through this class.
    """

    # Pin numbering
    PROJ_ON = 5
    SYS_RDY = 6
    HOST_IRQ = 19
    SPI_RDY = 7
    PRINT_ACTIVE = 13

    SPI_BUFFERSIZE = 65536  # note the default config for raspberry pi is 4096
    SPI_BUFFER_INDEX = 0  # FPGA buffer index that user can write to. Swapped after each image change

    addr = 0x1B  # i2c address

    def __init__(self, i2c_bus, spi_bus):
        """
        Checks if the DCLP1438 is running and ready for i2c communication, and if not, will 
        start the DLPC1438 with the PROJ_ON gpio signal.
        """
        print("Intialising the DLPC1438...")

        # Configure the pins
        GPIO.setup(self.PROJ_ON, GPIO.OUT)  
        GPIO.setup(self.SYS_RDY, GPIO.IN)  
        GPIO.setup(self.HOST_IRQ, GPIO.IN)  
        GPIO.setup(self.SPI_RDY, GPIO.IN)  
        GPIO.setup(self.PRINT_ACTIVE, GPIO.IN)  

        self.i2c = i2c_bus
        self.spi = spi_bus


        ## TODO: avoid this line below, which forces a full restart of the DLPC1438
        # I think it interferes with how the Anhua board is designed...
        GPIO.output(self.PROJ_ON, GPIO.LOW)    
        time.sleep(1)
            
        # there are 2 options (see figure 9.1 of DLPC1438 datasheet):
        # [1] host_IRQ is low, and the DLPC1438 has not started yet
        # [2] host IRQ is low, but the DLCP1438 is already active and running

        try:  # we try to communicate over I2C. This will trow I/O error if DLPC1438 is not active yet
            i2c_bus.read_byte(self.addr)  # check if i2c is already active. Then we are in [2]
            warnings.warn("DLPC1438 is already powered on when script initialised. No startup action needed.")

            # check the current active buffer
            self.SPI_BUFFER_INDEX = self.__i2c_read(0xC6,1)[0]
            print(f"Active buffer index at startup: {self.SPI_BUFFER_INDEX}")

            return
        except IOError:  # DCLP1438 seems to still be turned off (case [1]). Let's start it
            print("Setting PROJ_ON high to start DLPC1438 startup sequence... ")

            # send the PROJ_ON signal and wait for the HOST_IRQ signal to go high, signalling the DLPC1438
            # is ready to go
            GPIO.output(self.PROJ_ON, GPIO.HIGH)
            ref_time = time.time()
            while not GPIO.input(self.HOST_IRQ):
                time.sleep(0.01)

            print(f"DLPC1438 is signalling it is ready for use, {time.time()-ref_time} seconds after PROJ_ON went high.")

            # now we need to wait for I2C communication to be ready
            time.sleep(1)  # TODO: make this more robust

            # keep looping as long as we cannot find the DLPC1438 on the i2c bus
            while i2c_bus.read_byte(self.addr) == 0:  
                time.sleep(1)

            # check the current active buffer
            self.SPI_BUFFER_INDEX = self.__i2c_read(0xC6,1)[0]
            print(f"Active buffer index at startup: {self.SPI_BUFFER_INDEX}")

            return
        
    def __i2c_read(self, register, length):
        """Read I2C information from DCLP1438 at given register, expecting a certain number of bytes
        of data.
        
        This function exists primarily to keep a code more readable."""
        return self.i2c.read_i2c_block_data(self.addr,register,length)
    
    def __i2c_write(self, register, data):
        """Write I2C information from DCLP1438 at given register, sending a list of bytes specified
        in 'data'.
        
        This function exists primarily to keep a code more readable."""
        return self.i2c.write_i2c_block_data(self.addr,register,data)

    def switch_mode(self, new_mode):
        """
        Switch between DLPC1438 operational modes.

        Note that the input of the function must be an Enum of the Mode class.
        """
        # check that the new mode is actually a valid enum entry 
        if isinstance(new_mode, Mode):  
            print(f"> Switching DLPC1438 mode to {new_mode.name}\t (currently in {self.__i2c_read(0x06,1)[0]})")

            self.__i2c_write(0x05, [new_mode])  # send the new mode setting

            time.sleep(0.4)  # need some time to switch between modes

            # check that the mode switch was successful
            queried_mode = self.__i2c_read(0x06,1)[0]
            assert queried_mode == new_mode.value, f"Was unable to switch the DLPC 1438 to MODE:{new_mode}"

            # if we switched to EXTERNAL_PRINT mode, we will want to wait for 
            # SYS_READY to go high before doing anything else.
            if queried_mode == Mode.EXTERNALPRINT:
                self.__await_SYS_RDY()

        else:
            raise Exception("Invalid DLPC1438 mode provided. Use the Enum 'Mode', rather than the hex value.")
    
    def configure_external_print(self, LED_PWM, skip_FPGA_video=False): 
        """
        Apply various settings applicable to the EXTERNAL_PRINT mode of the DLPC1438.

        This function will configure multiple registers. Note that switching to STANDBY mode will
        likely reset some of these values, so it is suggested to call this just before switching
        to EXTERNAL_PRINT mode.
        """

        print(f"\nConfiguring the DLPC1438 for external print mode with LED PWM at {LED_PWM/1023*100}%")

        assert isinstance(LED_PWM, int), "LED_PWM must be a 10-bit integer"
        assert 0 <= LED_PWM < 1024, "LED_PWM must be 10-bit (i.e. in range [0, 1023])"

        # Write FPGA control (0xCA)
        # no CRC error injection, no CRC error calc, no FGPA reset, no FPGA reset unlock
        self.__i2c_write(0xCA, [0b00000000])  
        print(f"FPGA settings: {bin(self.__i2c_read(0xCB,1)[0])}")
        
        # write external print confugration (0xA8)
        # we choose a linear transfer function (byte 1) and select led 1 (byte 2)
        self.__i2c_write(0xA8, [0x00, 0b00000001])  
        print(f"External print settings: {self.__i2c_read(0xA9,2)}")

        # Write LED PWM current (0x54)
        # Set PWM value for LED 3/1
        print(LED_PWM.to_bytes(2, byteorder = 'big'))
        PWM_data = list(LED_PWM.to_bytes(2, byteorder = 'little')) + [0x00, 0x00, 0x00, 0x00]
        self.__i2c_write(0x54, PWM_data)  
        print(f"LED settings: {[hex(val) for val in self.__i2c_read(0x55,6)]}") 

        # Write parallel video (0xC3)
        # Enable the FPGA parallel video interface.
        if not skip_FPGA_video:
            self.__i2c_write(0xC3, [0x01])  
            print(f"prallel video settings: {bin(self.__i2c_read(0xC4,1)[0])}")

        # Write actuator orientation (0xC8)  # TODO: figure out if this one is really needed
        # see DLPC1438 programming guide for interpetation of these bytes. For now just using values of Elegoo board.
        self.__i2c_write(0xC8, [0x03, 0x16, 0x11, 0x06, 0x01])  
        print(f"Actuator orientation settings: {[hex(val) for val in self.__i2c_read(0xC9,5)]}")


    def  __await_SYS_RDY(self):
        while not GPIO.input(self.SYS_RDY):
            time.sleep(0.3)
            print("waiting for SYS_RDY")


    def expose_pattern(self, exposed_frames, dark_frames=5):
        """
        Start exposure of the buffer available to FPGA with a specified number of exposed frames.

        The FPGA outputs a ~60Hz parallel vide signal, so the exposure time (in sec) is roughly the
        number of exposed frames divided by 60. Note that you can also configure
        the exposure to continue indefinitely until the stop_exposure() command is called, by sending
        -1 as the number of exposed frames.

        Taking 5 dark frames is recommended if you call this command just after swapping image
        buffer. If you are doing other operations that take and equivalent amount of time
        after swapping the buffer before calling this function you could set this number to 0
        to increase frame throughput.
        """
        assert GPIO.input(self.SYS_RDY), "SYS_RDY signal is not high yet, cannot expose frames yet."
        assert isinstance(dark_frames, int), "dark_frames must be a 16-bit integer"
        assert 0 <= dark_frames < 65536, "dark_frames must be 16-bit (i.e. in range [0, 65535])"

        if exposed_frames > 0:
            assert isinstance(exposed_frames, int), "exposed_frames must be a 16-bit integer"
            assert 0 <= exposed_frames < 65536, "exposed_frames must be 16-bit (i.e. in range [0, 65535])"

            # start exposure of current buffer for the duration specifed in exposure time
            print(f"> Starting UV exposure (for {exposed_frames} frames / {exposed_frames/60:.2f}sec)!")
            frame_data = [0x00] + \
                list(dark_frames.to_bytes(2, byteorder = 'little')) + \
                list(exposed_frames.to_bytes(2, byteorder = 'little'))
            self.__i2c_write(0xC1,frame_data )
            # the value above never seem to be read back correctly if you read over I2C. Also on anyubic board.'

        elif exposed_frames == -1:
            # start exposure of current buffer for infinite duration with 5 dark frames to let video data stabilise)
            print("> Starting UV exposure (Infinite Duration)!")
            self.__i2c_write(0xC1, [0x00]
                              + list(dark_frames.to_bytes(2, byteorder = 'little'))
                              + [0xFF, 0xFF])  
            # the value above never seem to be read back correctly if you read over I2C. Also on anyubic board.'

        else:
            raise Exception("Invalid exposure time value provided. Value must be positive or -1.")

        time.sleep(0.02) # TODO: optimise delay time; now this is just quick empirical test
        if not GPIO.input(self.PRINT_ACTIVE): warnings.warn("PRINT ACTIVE did not go high after starting exposure. Something might be wrong.") 

    def stop_exposure(self):
        """
        Stop the UV exposure in external print mode
        
        This command is used to stop exposure in case the projector is set to 'indefinite' mode
        in the expose_pattern() command. This then allows the controller (e.g. raspberry pi) to
        control the start and stop time, rather than the DLPC1438. Can be useful in dynamic
        exposure settings, where the total exposure time is not known in advance.

        An alternative way to turn off the projector in indefinite projection mode is to turn
        it to standby mode, but that is not always the desired method.
        """

        print("Stopping UV exposure immediately!")
        self.__i2c_write(0xC1, [0x01, 0x00, 0x00, 0x00, 0x00])  

        time.sleep(0.1) # TODO: optimise delay time; now this is just quick empirical test
        if GPIO.input(self.PRINT_ACTIVE): warnings.warn("PRINT ACTIVE is still high after sending STOP uv expose command. Something might be wrong") 

    def __rowcol_data_block(self, col_start, col_end, row_start):
        """
        Format 4 byte data block containing column start/end and row start information for
        SPI transmission format of DLPC1438.
        """
        # the final 4 bits need to be 1 for reasons not explained, but let's just follow
        # the programmer's guide of DLPC1438
        rowcol_data_block_raw = col_start + (col_end << 5) + (row_start << 10) + (0b1111 << 28)
        rowcol_data_block = list(rowcol_data_block_raw.to_bytes(4, byteorder = 'little'))
        return  rowcol_data_block
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

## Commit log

2024-02-04 Add Raspberry Pi uHAT template
    [elegoo-dlp-controller.kicad_pcb, elegoo-dlp-controller.kicad_sch]
2024-02-05 Add initial draft of PCB
    [elegoo-dlp-controller.kicad_pcb, elegoo-dlp-controller.kicad_sch]
2024-02-07 change dc converter and switch to vertical connectors
    [elegoo-dlp-controller.kicad_pcb, elegoo-dlp-controller.kicad_sch]
2024-02-08 Connect SPI_RDY and minor retouching
    [elegoo-dlp-controller.kicad_pcb, elegoo-dlp-controller.kicad_sch]
2024-02-19 Initial basic version of code
    confirms that PCB version 0.1 is able to power the board and that is enables the bootup GPIO signals and I2c
2024-02-21 Add intial external print mode code
    Adds basic configuration options for EXTERNAL PRINT mode, as extracted from the I2C signals from the elegoo board.
2024-02-22 Implement early SPI transmission and minimal exposing code
    Added formatted SPI data transmission code. ALso changed some of the registers around to the point where the code will at least turn the projector mode in external print mode. The SPI data transmissi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
2024-02-28 Add 3D models to PCB
    Added some step files for the 3D view of the PCB. Will also be useful for the design of the enclosure.
    [PRT-14417--3DModel-STEP-SnapEDA.STEP, barreljack_DCJ200-10-A-K1-K-740395_SnapEDA.STEP, elegoo-dlp-controller.kicad_pcb, molex_5013310807.stp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]
2024-02-28 Add PCB readme and BOM
    [elegoo-dlp-controller.kicad_sch]
2024-03-02 Move to object-oriented and implement buffer swap, pwm, and exposure time
    Big refactor in moving to object oriented formulation for code. Cleaned up the code a bit with some convenience functions. Made into a more appropriate package form. Implemented the SPI buffer swap f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
2024-03-02 Update main readme
    Clean up current projec status and remove errant line.
2024-03-07 Fix SPI transfer and refactor functions
    Fixed issue with SPI transfer due to error in TI documentation. Images can now properly be displayed, even when updating only part of the frame. Multiple writes to the same buffer also works. Higher 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
2024-03-08 Add enclosure design files
    Add the design files for a basic 3D pritnable enclosure. Update documentation to contain some more information on dissembly of the printer and how to assemble the new unit.
    [dlp-controller-enclosure.FCStd, enclosure-base-elegoo.step, enclosure-base.step, enclosure-lid.step]
